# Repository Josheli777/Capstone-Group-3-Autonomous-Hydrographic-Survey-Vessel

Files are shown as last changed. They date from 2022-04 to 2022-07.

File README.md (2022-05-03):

# Capstone-Group-3-Autonomous-Hydrographic-Survey-Vessel

# Introduction: <br/>
Hydrography is the science of surveying and measuring different bodies of water, such as lakes, rivers, oceans, etc. These analyses are crucial for determining the shape of the water body. This data obtained from hydrography can be used to monitor the effects of climate change, beach erosion, and natural disaster prediction. Additionally, civil engineers must know the layout of a body of water before starting projects like dredging, diverting water sources, building docks, etc. The Tennessee Water Center currently has boats that take hydrographic projections that are remote-controlled; however, this technology is prone to human error and lacks efficiency that could be further improved by automation. There are currently autonomous vehicles that take measurements accurately and precisely. These boats take GPS coordinates and create parallel lines for the boat to travel to retreive less repetitious measurements.  The Water Center has contacted us to design a boat that has similar functionality to commerically avaialble hydrographic boats but at a significantly lower cost. The Water Center has asked that the boat can transmit GPS data and depth measurements in real time to allow surveyors to determine if data is accurate. If the data is not accurate, the team will be able to immediately bring the boat back to land base and not have to wait for the boat to complete its run. 

# Project Capabilities: <br/>
* Navigating bodies of water using a predetermined path
* Calculate its GPS location with centimeter level precision and accuracy
* Transmits GPS data and battery cell voltages for monitering
* Switches between manual and autonomous control through a remote controller switch
* Navigate bodies of water at a speed of 3ft/s for about 3 hours.

# Salient Outcomes: <br/>
## Battery Testing and Monitoring: 
The Water Center has requested that the autonomous hydrographic surveying boat have a run time of at least one hour and an accurate battery monitoring system. The current design of the power subsystem allows surveying teams to operate the boat for approximately 3 hours by use of 2 Liperior Lithium-Polymer batteries (14.8 V, 22000 mAh) connected in parallel. Additionally, 2 quad op-amp circuits were constructed and implemented that provide voltage readings of each cell in the Liperior batteries. These voltages can be verified by using the battery charging station that displays the actual cell voltages. 

## Data Transmission:
The specification to communicate data such as hydrographic measurements, GPS location, and battery voltage levels from the boat to a land base in real time has been addressed by the data transmission subsystem.  A pair of Arduino Unos and two nRF24L01+ radio modules were used in the subsystem design. The subsystem uses 2.4 GHz radio frequency (RF) to transmit the collected data to the base station PC. This system tested on Cane Creek, and it was confirmed that it could reliably transmit GPS data and battery voltage levels measured from the onboard battery monitoring system. The most up-to-date version of this system had a reliable connection at up to 550 meters and was transmitting GPS and battery data successfully. Additional work will be needed to complete the integration with the sonar system in order to transmit hydrographic data. 

## GPS Accuracy and Precision:
The use of Real-Time-Kinematic GPS receivers allowed us to achieve GPS data with much more accuracy than normal receivers. This project makes use of two simpleRTK2b receivers with a long-range transmission to receive latitude and longitude coordinates with centimeter level accuracy and precision. The two receivers are set up in a base and rover configuration. This allows the “rover” receiver, which is on the boat itself, to receive RTCM corrections from the “base” receiver which is connected to a PC on land. For this project, centimeter level accuracy and precision is required for the boat to navigate the predefined path. This can only be achieved if the location of the PC with the base station is known and uploaded to the base station receiver. After testing this configuration, the accuracy was found to be 2 cm and the precision was about 3 cm. 

# Video of Project Testing: <br/>
Full test (all systems communicating): https://youtu.be/emZcUE4ue-M

# Video of Experimental Analysis: <br/>
Battery Testing: https://www.youtube.com/embed/ibnFtC95N1E <br/>
Data Transmission Range Testing: https://www.youtube.com/embed/1JbO_NOVdsQ <br/>
Speed Testing: https://www.youtube.com/watch?v=HDup7zcuE3E&t=6s <br/>
GPS Accurcy & Precison Testing: https://www.youtube.com/watch?v=qKELYZJ67d8&t=15s <br/>
Switching Between Autonomous and Manual Control Testing: https://www.youtube.com/watch?v=emZcUE4ue-M&t=8s <br/>
Updated Battery Monitor: https://youtube.com/shorts/7BtCwoOhJbw?feature=share <br/>

Updated code attempting to navigate: https://youtube.com/shorts/_wtcSN0W4yQ <br/> 

# Images: <br/>
  Boat Prototype <br/>
  Autonomous Hydrographic Boat Prototype
 
# About Us: <br/>
The team members involved in the construction of the autonomous hydrographic boat are Andrew Alley, Carter Ashby, Levi Daniel, & Joshua Herrera. Mr. Jesse Roberts provided guidance and insight thoughout the duration of the project. This project was funded by Dr. Alfred Kalyanapu on behalf of the Tennessee Tech Water Center.

# Repository Contents: <br/>

### Project Documentation:
Bill of materials for the project and schematics for each subsystem.

### Reports:
Reports that document the design process for this project.

### Software:
Guides for installing computer applications, programming libraries, and operating systems necessary for this project.

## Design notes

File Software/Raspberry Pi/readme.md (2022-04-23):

# Raspberry Pi:
Parts Needed:
  * Keyboard
  * Mouse
  * 16 GB micro SD card
  * micro SD card reader
  * micro HDMI to HDMI cable
  * 5V 3A power cable

Installing Raspberry Pi OS
Download Raspberry Pi Imager:
https://www.raspberrypi.com/software/

* Insert micro SD card into PC using micro SD card reader
* Open Imager
* Click "Choose OS"
* Click "Raspberry Pi OS (32-bit)
* Click "Choose Storage" and select the inserted SD card
* Click "Write"
* Eject SD card when done

Setting up the Raspberry Pi
* Insert micro SD card into Raspberry Pi
* Connect mouse and keyboard
* Connect Raspberry Pi to monitor through left micro HDMI port using adapter cable
* Connect Raspberry Pi to power
* Follow on screen instructions to setup Raspberry Pi OS

Upgrade the Raspberry Pi:

```
sudo apt update
sudo apt full-upgrade
```
 
Install git if not installed already
```
sudo apt install git
```

Install pip
```
sudo apt get-install python3-pip
```

Install numpy
```
pip install numpy
```

Install proj
```
pip install proj
```

Install pyproj
```
pip install pyproj
```

Install stateplane
```
pip install stateplane
```

In order for the Raspberry Pi to interface with the GPS receiver, type the following command:
```
sudo raspi-config
```

Select Interfacing Options, Serial, No, Yes, Finish

Now you can use the python program above. <br/>

To enter a predetermined path into the program, enter a list of latitude points into the lats[] list and enter longitude points into the lons[] list.
Change the countyfips value to the one corresponding to your state and county.

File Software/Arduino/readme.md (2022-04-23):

# Arduino

## Software Description
Two Arduino Uno's are currently used to read GPS data, control the battery monitoring subsystem, and transmit/receive data using the nRF24L01+ radio modules.

### Rover Arduino:
The script "ROVER_full_function.ino" was written to control the Arduino on the rover. The serial baud rate should be set in 'setup()' to match the output baud rate of the simplertk2b GPS. Commands to start and configure the nRF24L01+ radio module and initialize pins for the battery monitoring task are also written in the 'setup()' function. The radio module is setup as the transmitter.<br/><br/>
The 'loop()' function contains the instructions for the primary functionality of the onboard Arduino. The program checks the Arduino's serial buffer for GPS data, and if data is found, it reads it and sends it to the radio module for wireless transmission. If no data is found in the buffer, a message that says "NoData" is transmitted by the radio module.<br/><br/>
Next, the 'BatteryCheck()' function is called. The function uses two GPIO pins to control the select lines of the 4 to 1 multiplexers. Two analog input pins on the Arduino are used to read the voltage levels of the multiplexer outputs. The program cycles through each of the battery cell voltage levels by changing the values on the select lines. The select line values are written to the appropriate pins in the 'SelectLineOut()' function. The voltages are converted from what the analog pins return to the actual voltage value. These voltage values are sent to the radio modules for transmission. The program continues by starting the next iteration of the 'loop()' function.

### Base Station Arduino:
The script "BASE_RX.ino" was written to control the Arduino at the base station. This Arduino will be connected to the technician's computer via its USB port. Commands to start and configure the nRF24L01+ radio module are written in the 'setup()' function. An if statement checks if the radio module starts successfully. The radio module is setup as the receiver.<br/><br/>
The 'loop()' function checks if the radio has received any transmissions, and if it has, it reads the information and outputs it to the Arduino serial buffer.

## Dependencies
The Arduino SPI library is used in both scripts to communicate to the nRF24L01+ modules using SPI protocol.<br/><br/>
The external RF24 library is used to control the radio modules in both scripts. https://github.com/nRF24/RF24 <br/><br/>
The Arduino SoftwareSerial library is used by the rover Arduino to make two GPIO pins (2,3) function as serial pins (TX/RX).

## Installation
Both .ino files can be downloaded and opened in the Arduino IDE. To upload the scripts to the Arduinos, connect the computer running the IDE to the USB port of the approprate Arduino and select "Upload". Note that the .ino files must be in a folder of the same name (excluding the '.ino') to upload properly. When the "Done uploading" message is displayed, the program will now execute on power-on until it is overwritten by another program. For more details on using the Arduino IDE follow https://docs.arduino.cc/learn/starting-guide/the-arduino-software-ide

## How to Operate
Refer to the design schematics to connect power and onboard components to the rover Arduino. The uploaded program will execute at power-on.<br/><br/>
The base station Arduino should remain connected to the base station computer via USB. The data received from the rover can be viewed by clicking Tools->Serial Monitor and changing the baud rate to match the baud rate set in the "BASE_RX.ino" script.

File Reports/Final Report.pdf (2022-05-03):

# Autonomous Hydrographic Survey Vessel

Andrew Alley
Department of Electrical
Engineering
Tennessee Tech University
Cookeville, TN
atalley42@tntech.edu

Carter Ashby
Department of Electrical
Engineering
Tennessee Tech University
Cookeville, TN
cashby42@tntech.edu

Levi Daniel
Department of Electrical
Engineering
Tennessee Tech University
Cookeville, TN
lbdaniel42@tntech.edu

Joshua Herrera
Department of Electrical
Engineering
Tennessee Tech University
Cookeville, TN
jherrera42@tntech.edu
I. INTRODUCTION
Bathymetry is the science of measuring and observing the depths of different bodies of water, such as lakes, rivers, oceans, etc. These analyses are crucial for determining the shape of the water body. Furthermore, data obtained from bathymetry can be used to monitor the effects of climate change, beach erosion, and subsidence. The Tennessee Tech Water Center also uses bathymetry to create simulations to predict natural disasters and locations that are more susceptible to flooding.

The Water Center currently uses remote-controlled boats that take bathymetric projections by navigating the boat back and forth across the body of water. Performing this task manually is labor-intensive and prone to error. Depending on the size of the body of water, it could take several days to collect all the necessary data. The resolution of the data is also too low to create a useful bathymetry map. There are autonomous hydrographic survey vessels (HSV) commercially available; however, these products greatly exceed the budget of the Water Center with autonomous HSVs starting at a price of $70,000.

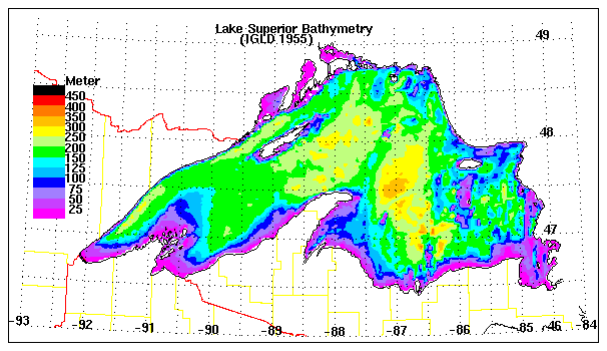
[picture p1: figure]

Figure 1: Bathymetry Map of Lake Superior

A. Overall Idea
The requirement to deliver a boat that will navigate the entirety of a body of water without direct control from the user will be met by constructing a watercraft driven by software that intelligently plots and follows a course that will allow the boat to collect measurements over the full area of the body of water. To collect the required bathymetry data samples the boat will be equipped with sonar and GPS. A sonar sensor is the most likely solution for depth measurement device. An accurate GPS-generated location reading will be recorded with each sonar measurement, and data processing software will be used to generate maps and charts from the collected data. A software application will also be developed that will allow someone onsite to transmit commands to the boat while also being able to view the collected bathymetry data in real time.
B. Constraints and Regulations
The boat was given these initial specifications:
- The boat must successfully measure the entirety of Cane Creek Lake (56 acres) in one test run
- The boat needs to travel at a speed of 3-5 ft/s to ensure accurate sonar data measurements
- Data such as hydrographic measurements, GPS location, and battery voltage levels need to be transmitted from the boat to a land base in real time.
- The users on the land base need to be able to switch between manual and autonomous control.
- Obstacle avoidance needs to be implemented to prevent any collisions when the boat is in autonomous control.
- An abort option needs to be implemented if the boat is receiving inaccurate data measurements.
- The overall design and construction price should not exceed commercially available HSVs.
- The design must be easily replicable for any group interested in using this project to take their own hydrographic measurements.

The regulations that govern remote control radio signals require that the boat only be controlled via radio signals in the 26-28 MHz band and that power output from the transmitter be no more than 4 Watts. The radio signals used to control the boat must also only control the boat; they cannot be used to transmit data from the collection process [5].

The regulations that govern Wi-Fi signals require that Wi-Fi frequencies be restricted to 902-928 MHz, 2400-2483.5 MHz, or 5725 to 5875 MHz, as they are considered unlicensed wireless equipment devices [6]. The transmitter is also required not to exceed a peak output power of 1 Watt, and the Effective Isotropic Radiated Power (EIRP) cannot exceed 4 Watts [7]. The EIRP is simply a combination of the output power and the antenna gain.

II. SALIENT OUTCOMES

A. Battery Capacity and Monitoring:
The Water Center has requested that the autonomous hydrographic surveying boat have a run time of at least one hour and an accurate battery monitoring system. The current design of the power subsystem allows surveying teams to operate the boat for approximately 3 hours by use of 2 Liperior Lithium-Polymer batteries (14.8 V, 22000 mAh) connected in parallel. Additionally, 2 quad op-amp circuits were constructed and implemented that provide voltage readings of each cell in the Liperior batteries. These voltages can be verified by using the battery charging station that displays the actual cell voltages.
B. Data Transmission:
The | specification | to | communicate | data | such | as
hydrographic measurements, GPS location, and battery voltage levels from the boat to a land base in real time has been addressed by the data transmission subsystem. A pair of Arduino Unos and two nRF24L01+ radio modules were used in the subsystem design. The subsystem uses 2.4 GHz radio frequency (RF) to transmit the collected data to the base station PC. This system tested on Cane Creek, and it was confirmed that it could reliably transmit GPS data and battery voltage levels measured from the onboard battery monitoring system. The most up-to-date version of this system had a reliable connection at up about 550 meters and was transmitting GPS and battery data successfully. Additional work will be needed to complete the integration with the sonar system in order to transmit hydrographic data.
C. GPS Accuracy and Precision:
The use of Real-Time-Kinematic GPS receivers allowed us to achieve GPS data with much more accuracy than normal receivers. This project makes use of two simpleRTK2b receivers with a long-range transmission to receive latitude and longitude coordinates with centimeter level accuracy and precision. The two receivers are set up in a base and rover configuration. This allows the “rover” receiver, which is on the boat itself, to receive RTCM corrections from the “base” receiver which is connected to a PC on land. For this project, centimeter level accuracy and precision is required for the boat to navigate the predefined path. This can only be achieved if the location of the PC with the base station is known and uploaded to the base station receiver. After testing this configuration, the accuracy was found to be 2 cm and the precision was about 3 cm.

III. OUTLINE OF REPORT
The objective of this paper is to present the problem that this project aimed to solve and the steps in developing the solution. The goal of this project is to develop an autonomous machine that measures the depth of bodies of water. These measurements will then be used to create an accurate bathymetry map of the lake, river or pond that is being mapped.

The rest of this paper will describe the science and engineering behind this project and the process by which this project was completed.

IV. LITERATURE REVIEW
Two of the commercially available products for autonomous HSVs are the CEE USV from CEE Hydro Systems, and the Seafloor HyDrone-RCV survey boat by FLT Geosystems. Both boats allow the user to switch between manual and autonomous navigation. They are both used for taking hydrographic surveys of bodies of water using autonomous navigation. We modeled our original idea for the navigation program after these products.

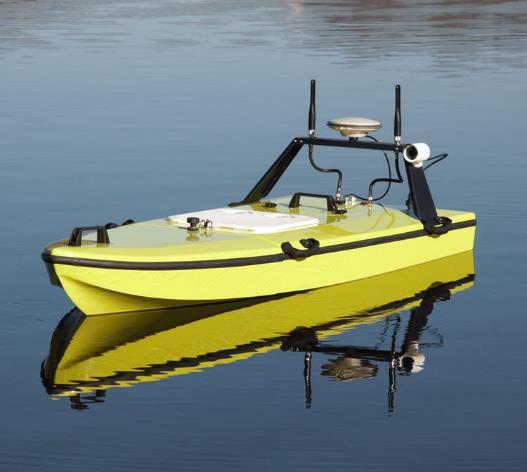
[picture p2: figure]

Figure 2: CEE USV

The main difference between our project and these products is the cost and functionality of the devices. The CEE USV has been noted to be upwards of $70,000 and the HyDrone-RCV with the autonomous navigation upgrade is around $15,000. One of the biggest cost cuts came from the RTK GPS receivers. The CEE USV uses a receiver that is well over a few thousand dollars while we are using a simpleRTK2b receiver kit which is less than $900 [12].

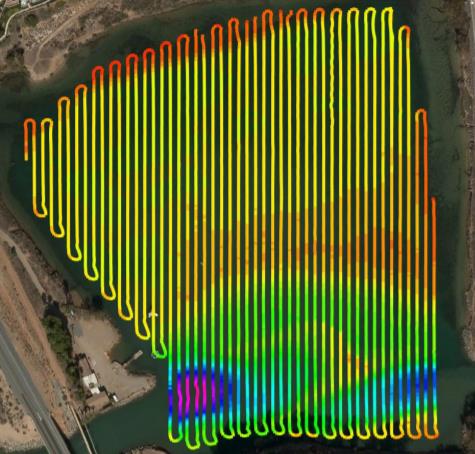
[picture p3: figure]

Figure 3: Intended Path Generation Method

The method of autonomous navigation is also a significant difference between the commercial products and our project. This model uses a predefined path that is specific for the body of water that needs to be surveyed. These paths can be easily generated using path planning software such as ArduPilot. The

GPS points can be entered into the autonomous program and the Raspberry Pi will process them and use them as waypoints.

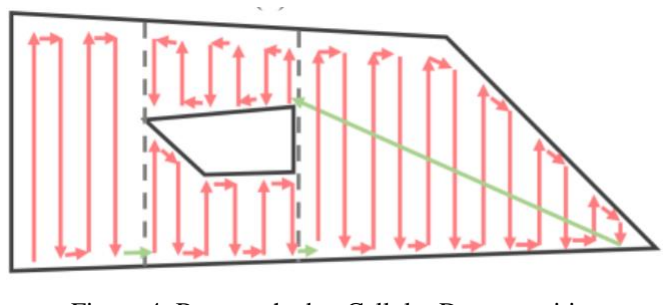
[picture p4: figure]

Figure 4: Boustrophedon Cellular Decomposition

Originally, we planned to use an algorithm known as Boustrophedon cellular decomposition. This is a commonly used path planning method to effectively cover large surfaces such as fields [13]. Autonomous lawn mowers use this method to cover entire fields efficiently. This method involves splitting an area up into sections and determining the best path to follow in order to minimize travel distance and travel time. Unfortunately, we were not able to incorporate this due to time. So, the previously mentioned method of predefining a path was used instead.

V. DESIGN PROCESS
The Water Center has asked us to develop an autonomous vessel that is capable of navigating a given body of water. The specifications include that the boat should be able to navigate Cane Creek Lake within its battery life as well as travel at optimal speeds for bathymetric data collection. The boat must also be able to transmit data back to an on-land computer. The design that was implemented for this project includes a navigation system, power system, and data transmission system. The purpose of the navigation system is to make the boat autonomous while keeping the boat at a specified speed and keeping the boat on a path that is optimal for bathymetric data collection. The power system is responsible for distributing power to each component and regulating voltage supplies. The data transmission system transmits GPS data, battery voltages, and eventually sonar data.
A. Original Navigation System
The manual control portion of the navigation system will assist in meeting the specifications that the boat will be autonomous and that the boat will have an abort operations function. For the boat to be able to autonomously navigate the body of water, the GPS coordinates of the perimeter of the lake must be measured. This process will require the user to manually drive the boat around the lake with a controller. The manual control system also needs to have programmable inputs for the abort function. In an emergency the user will press a button on the manual controller that tells the boat to stop collecting sonar data and return to the user. The user will also be able to tell the boat when to start collecting perimeter data, when to switch to manual control, and when to begin autonomous navigation. These will be assigned to inputs on the remote controller by the user. These functions were determined to be necessary to improve autonomy or ease of use.

The components that will be used for this system include the Spektrum DX6E controller and the Spektrum AR620 receiver. The decision to use this controller and receiver is based on its available programmable switches and its ability to operate the current boat model that was built by the Water Center at TN Tech. This was observed when a test run was conducted with the current boat model on Cane Creek Lake. The Spektrum controller will allow the project to meet the specification that the boat will be able to collect bathymetric data, the boat will be autonomous, and the boat will have the ability to abort data collection in case of an emergency. For the boat to begin collecting bathymetric data, it will need to be driven manually around the perimeter of the lake so that GPS data for the lake can be recorded. To do this, the Spektrum controller and receiver will need to output a signal that can control the electronic speed controllers (ESCs) that control the motors of the boat. This was observed by test driving the current model of the boat which implemented the Spektrum controller and receiver as well as Blue Robotics Basic ESCs and Blue Robotics T200 brushless thrusters. These are the same ESCs and thrusters that will be implemented in the autonomous boat. The range for the receiver is listed as 2 kilometers [1]. This distance is suitable for the purposes of navigating Cane Creek Lake. The length of Cane Creek is just over half a mile and since the user must always be able to see the boat, it will be easy for the user to stay within range. This controller also has extra switches on it that can be programmed for desired functions [2]. These switches can be assigned to the receiver outputs which will connect to the Raspberry Pi 4 in the onboard navigation system. These will control the boat’s mode of operation.

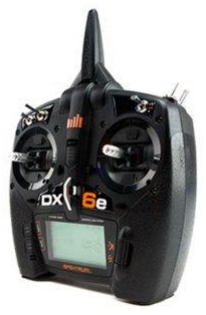
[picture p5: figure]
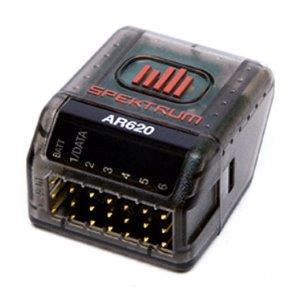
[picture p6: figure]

Figure 5: RC controller and Receiver

B. Navigation System (Autonomy)
The autonomous portion of the navigation system will directly meet the specification that the boat will be autonomous. It will use a GPS device to record data for the perimeter of the body of water. A microcontroller will process this data and create a path for the boat to travel that is optimal for sonar data collection. The microcontroller will then send signals to the motors that control the thrust to steer the boat along the created path. Signals from the user will be sent to the microcontroller to adjust the boat’s mode of operation.

The Blue Robotics T200 thrusters are currently what the Water Center has for an old model of the boat. The Blue

Robotics T200 thruster will be able to meet the specification that the boat should move at 1-3ft/s. Using the CAD files for the hull of the boat, an estimate of the weight was calculated. The total volume of the hull was found to be 9,381 cm^3. To be safe with the calculation of the hull’s weight, the highest density 3D printed material was used which was 2.16g/cm^3. Multiplying these two values results in a total weight of 20.264kg. This equates to an estimated weight is 44.67lb. The total weight of the hull and other components turns out to be about 52.18 lb. The maximum thrust of the T200 motors is 11.6lb of force [3]. Assuming the boat will accelerate to the desired speed of 3 ft/s or 0.9144 m/s within 1 second, the acceleration will need to be 0.9144m/s/s. Using the equation F = m*a, the force needed to accelerate a mass of 52.18lbs or 23.67kg at a rate of 0.9144m/s/s would be 21.64 Newtons or 4.86lbf. This is well within the capabilities of the T200 motor.

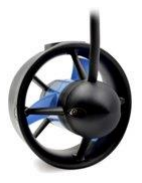
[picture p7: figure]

Figure 6: T200 Thruster

The Blue Robotics ESCs will be able to control the motors since these ESCs are specifically designed to control T200 or T100 motors. These ESCs are what the Water Center is currently using for their model of the boat. Here is a performance chart that displays the thrust of the T200 motor with different operating voltages while using the Blue Robotics Basic ESC R3 [3]. From the chart the thrust is highly adjustable using the Basic ESC R3 and adjustments to the operating voltage.

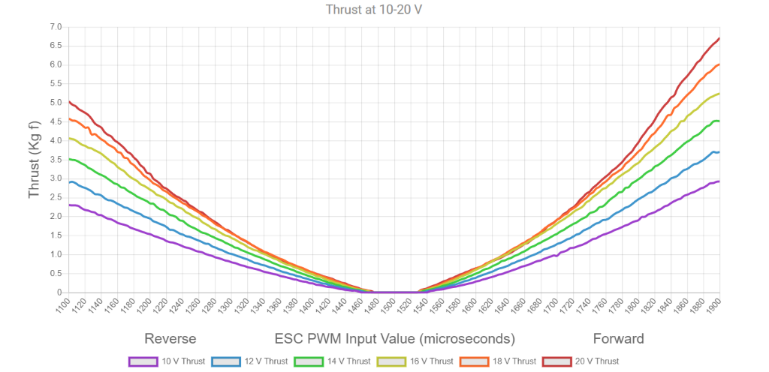
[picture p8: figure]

Figure 7: T200 Thruster Performance Chart

Figure 8: Blue Robotics Basic ESC

The Raspberry Pi 4 is necessary to meet the specification that the boat will be autonomous. The Raspberry Pi 4 will have ROS installed and the appropriate drivers necessary to process the GPS data from the simpleRTK2b board. The Raspberry Pi 4 will be capable of controlling the ESCs based on the documentation for both components. There are designated pins on the Raspberry Pi that can produce a PWM signal which is the required input signal for the ESCs [4][5]. Also, the voltage output of a Raspberry Pi 4 is 3.3V which is within the 3.3V-5V range required for the operation of the ESC [4][5].

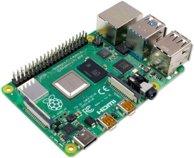
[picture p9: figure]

Figure 9: Raspberry Pi 4 B

The simpleRTK2b long range kit will allow the project to meet the specification that the boat will collect bathymetric data and that the boat will be autonomous. This kit will allow the Raspberry Pi to know its latitude and longitude to within a few centimeters [6]. The boat will be driven around the perimeter of the lake before the sonar data collection begins. The GPS data for the perimeter of the lake will be processed by an ROS program in the Raspberry Pi to create a path that the boat will travel while it is collecting bathymetric data. Centimeter level accuracy is necessary to produce sufficient data to create bathymetric maps. The simpleRTK2b LR kit will be able to communicate NMEA protocol data messages that contain the GPS coordinates [6]. This kit provides two simpleRTK2b boards. They will be set up in a “base and rover” configuration in which one board will be on the boat and one will be in a fixed position with a clear view of the sky. This allows the position of the boat to be calculated to within a few centimeters. This is necessary for the generated path to be optimal for sonar data collection. The GPS data is transferred between the boards using two antennas and two XBee radio modules [6]. The range of this kit is 10 km which exceeds any limitation set by the controller or other systems [6].

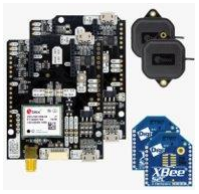
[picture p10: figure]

Figure 11: SimpleRTK2b Long Range Kit

The 4-channel mux will assist in meeting the specification that the boat will have an abort function. In case of an emergency, the user will flip a switch on the Spektrum RC controller. This will send a signal to the Raspberry Pi which will toggle one of the select lines on the mux [7]. The output of the mux will switch from the Raspberry Pi's motor control signal to the RC receiver's motor control signal. The simpleRTK2b adapter for the Raspberry Pi 4 will be used for its intended use case which is to connect a Raspberry Pi 4 to a simpleRTK2b board [8].

C. Navigation System Changes
The original design of the navigation system included a microcontroller, steering mechanism, manual control, mapping software, obstacle avoidance system, and a GPS system. While most of these components and concepts remained, the functions of each component were changed. For the microcontroller, we ended up using a Raspberry Pi 4b with 4 GB of RAM. The intended functions of the Raspberry Pi included processing GPS data, sending GPS data to a mapping software on an on-land PC, controlling the thrusters to keep the boat on the generated path, and to avoid obstacles. Of these functions, the final product processed GPS data and controlled the thrusters. We decided that obstacle avoidance would be taken care of by switching the boat to manual control and driving around the obstacle. The original plan for generating the path was by recording the perimeter of the lake and having the Raspberry Pi process the data and generate a zig-zag path across the lake. In the end we decided that software such as Ardupilot could be used to generate the waypoints of the path and the Raspberry Pi will handle the rest. Switching between manual and

Figure 10: Full Navigation Schematic

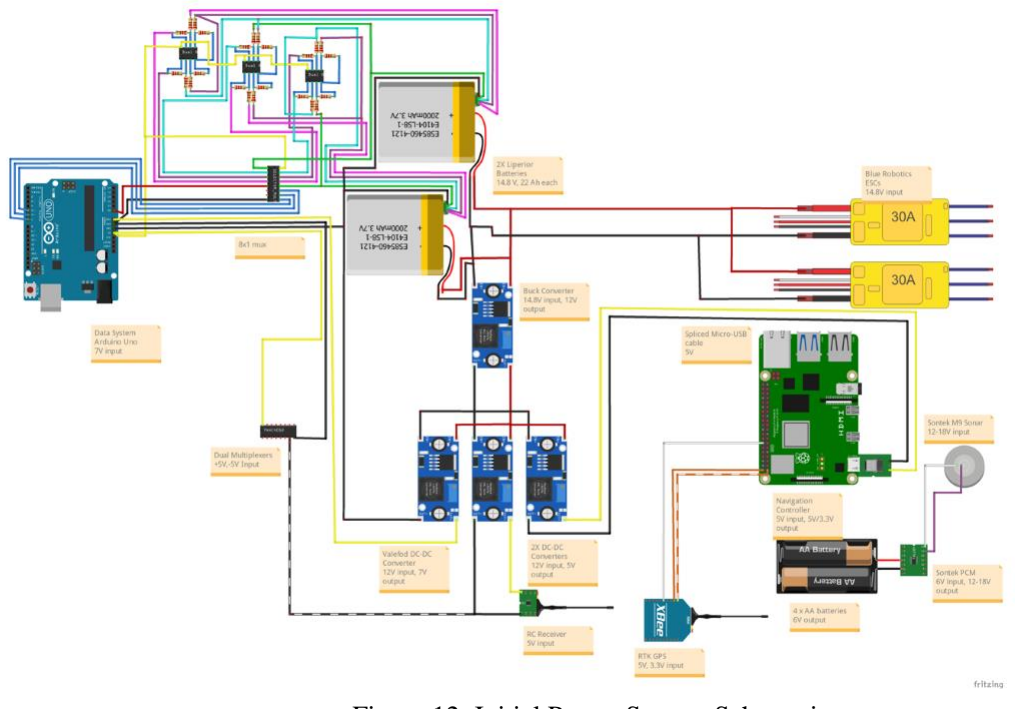
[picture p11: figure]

autonomous was originally going to be done by sending a signal to the Raspberry Pi through the remote control. Then Pi would then control the select lines of an analog mux that switched which device was controlling the thrusters. The use of ROS to create the autonomous program was scrapped as well due to issues with installation and usability of Ubuntu Mate. We ended up using Raspberry Pi OS which is not compatible with ROS.

D. Power System Initial Design:
Understanding the power requirements for each individual component was critical to the decision on battery selection. A compromise was necessary to balance the physical size and weight of the battery or batteries in order to keep the boat afloat and maneuverable, with the voltage and current it could supply and the period of time it could last. It was determined that two 14.8 V, 22000 mAh batteries were the best choice. They weigh 3.75 lbs each, which is negligible compared to the weight of the boat and its buoyancy. Connecting the two batteries in parallel extends the time that the given capacity can last, as the electronic systems draw power from each boat evenly, reducing the drain on a single battery by 50%.

These batteries are needed to provide the appropriate voltages to the Arduino, Raspberry Pi, and RC receiver. To address this, a buck converter was implemented on each component with the batteries as the input. The output of a buck converter is directly proportional to the input by what is known as a duty ratio. If the input voltage of a buck converter was to increase, the output was also decrease at a proportional rate, and if the input voltage of a buck converter decreases, the output also decreases. The input of the buck converters needed to maintain a constant voltage even though the batteries’ voltages would eventually decrease. A buck-boost converter was then designed into the circuit to provide a constant 12 V to the buck converters.

Both buck and buck-boost converters output voltages with some ripples. These ripple voltages described in their datasheets were too large and would damage the components if left as is. To rectify this issue, filters were placed at the outputs of all the converters.

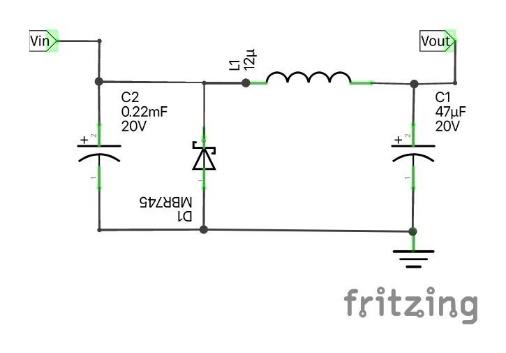
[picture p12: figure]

Figure 13: Buck Filter

Measuring the batteries voltage output was necessary for monitoring the capacity, since the battery voltage must be within an optimal range for the ESCs to operate. If the battery drops below this voltage, the operation will be less than optimal. The voltage measured by the Arduino Uno will be compared to the optimal voltage. If it is less than the optimal voltage, the Arduino Uno will send a signal to the Pi. The Pi will change the course of the boat to the starting point so that the user can recharge the batteries. The Liperior batteries consist of 4 cells that are each 3.7 V. The voltage of each cell needs to be above 3.5V to be within optimal operating voltage. If the batteries drop below this voltage, there is a risk of damaging the batteries. The batteries have a balance plug that is connected to each of the cells in the battery. These were used to measure the voltage of each of the cells. The Arduino Uno compares each of the 8 battery cells voltages to see if they are above 3.5 volts. This was done using an 8x1 multiplexer and differential amplifier circuits. The Arduino Uno is only capable of measuring voltages of up to 5

Figure 12: Initial Power System Schematic

V. Since the batteries are connected in series, the output voltages from the balance plugs were predicted to be 3.7 V, 7.4 V, 11.1 V, and 14.8 V. There were going to be 6 differential amplifier circuits. The team planned to use 3 dual op amp ICs. Each circuit used would have consisted of four 1.0 kΩ resistors. The output would have been the difference between two of the battery cells. An 8x1 mux will be used to multiplex the voltages. The Arduino controls the select lines and "loop" through the voltages and measure each battery cell. The multiplexers and the dual op-amps were to be powered by the same 5V pin that is powering the other mux. The mux needs between 4.5 and 5.5 volts to power it.

The thrusters have a maximum current draw of 20 A at 14 V each, when operating at full throttle. The required thrust calculated to maintain the specified boat speed was approximately 4.86 lb*f or 2.20 kg*f. The thrusters can provide this amount of force while drawing approximately 6 A at 14 V. This was assumed to be the average current required from a single thruster. The Raspberry Pi 4 B itself has a maximum current draw of 3 A and 1.2 A for any peripheral components, such as the GPS device. The Arduino board has a wide range of current draw depending on the purpose of operation, with the maximum being approximately 100 mA. The RC receiver, when the boat is operating in manual mode, will allow the thrusters to draw the same amount of current that they would draw operating in autonomous mode. The maximum continuous current draw for the receiver itself is 3 A. Then the total average current draw of all systems during normal operation is approximately 21.87
A. The current draw may have been more or less, depending on the throttle of the motors, data collection, and data transmission. Each Liperior battery has a capacity of 22 Ah. When connected in parallel, the combined capacity will be 44 Ah, which will provide a runtime for the boat of approximately 2 hours. This met the Water Center’s desired specification to have the
autonomous | boat | operate | for | at | least | 1 | hour.
E. Power System Changes:
Once the team received the desired components, circuit construction and analytical testing were done by using solderless breadboards. The buck converters were sufficient in outputting the required voltage ranges of operation to the Raspberry Pi, Arduino, and RC receiver. The filters were successful in reducing the ripples of the buck converters from 60 mV to approximately 30 mV. When testing the buck-boost converter, however, the output ripple was significantly larger than predicted. The designed filter’s capacitors were then modified in a series of analytical testing to reduce this ripple, but testing proved unsuccessful. The team then backtracked and reviewed the behavior of the buck converters that were received. The output of a buck converter was set to 5.0 V, and the input was set to 14.8 V on a DC power supply. This input was then changed to determine how the output voltage would be affected. It was concluded that the buck converters kept a constant output voltage if the input was at least 1.0 V greater than the output. The team then concluded that the buck-boost converter was not necessary and removed it from the power subsystem.

Once the batteries came in, the balance plug could be tested. It was found that all 4 cells of each battery would need to be implemented into the differential amplifier circuits. Instead of using 3 dual op-amps, the team decided to use 2 quad op-amp

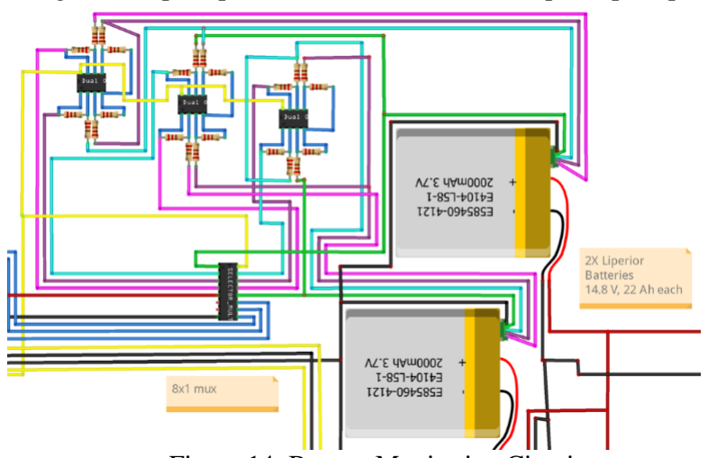
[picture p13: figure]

Figure 14: Battery Monitoring Circuit

circuits with 4 equal resistors with each individual circuit. Another issue arose when observing the output pins of these circuits. Most of the pins would output accurate readings, but some pins would have voltages ranging from 5-10 V. This was due to the lack of negative voltage supply that the team initially thought was unnecessary. A temporary solution was to use two 9 V batteries with one of the polarities reversed. This was not optimal for the final design, for teams would not be able to realistically monitor the capacities of the 9 V batteries. This was then addressed by implementing an inverter IC. The input of the IC is the Liperior batteries. The positive output is connected to V⁺

, and the negative output is connected to V⁺
. Testing then
verified that the voltages of the outputs were consistent with the individual battery cell readings that are displayed on the battery chargers.

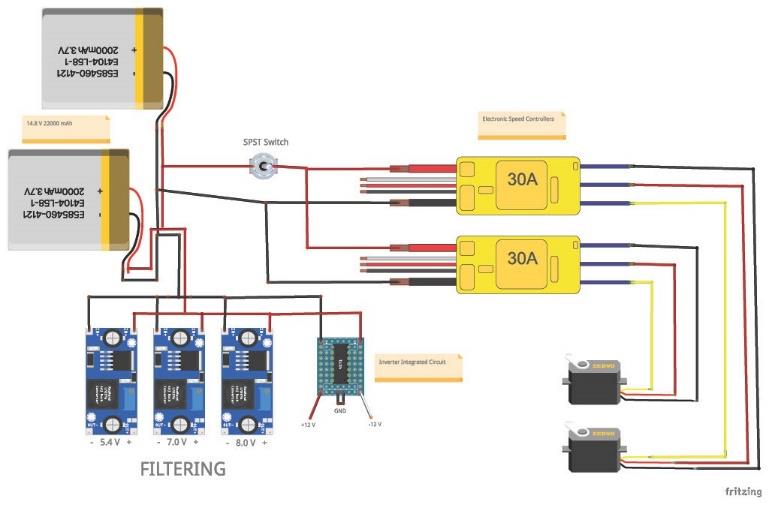
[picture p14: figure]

Figure 15: Final Power System with Dual V+ and V- Supply

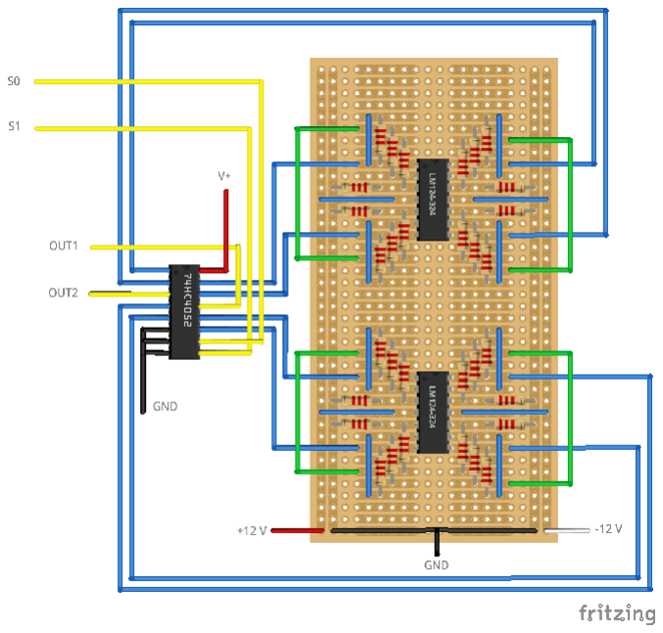
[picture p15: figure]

Figure 16: Updated Battery Monitoring Circuit

F. Transmission System Initial Design:
To meet the requirement to observe data in real-time as it is collected, a system has been designed to collect measured data and transmit it to a local computer system so it can be viewed by the user. The design of this system has evolved over the course of this project according to new knowledge and changes of ideas.

The original conceptual design of the data transmission system was split into two main parts: the base station section and the onboard section. The design for the onboard section included a microcontroller to collect data from the onboard systems and an RF transmitter to send the data to the base station. The design for the base station section included a microcontroller and an RF receiver. The microcontroller was connected to the base station PC with a USB connection, and it was designed to be used to operate the RF receiver and communicate the received data to the PC. Also, the designs assumed the SonTek HydroSurveyor sonar system would be used and included the SonTek Power and Communications Module (PCM) as the primary method for the transmission of hydrographic depth data.

When first selecting components for the conceptual system, a pair of 433 MHz RF modules was selected for the transmitter and received components. At the time of the detail design, the decision was made to use 2.4 GHz modules instead. The first reason this change was made was because in the United States the 433 MHz frequency band is restricted by the FCC to only certain licensed devices. Secondly, although 433 MHz frequency transmitters offer much greater range for the same transmission power, 2.4 GHz devices can support much greater message signal bandwidths. In addition, the connection for the onboard GPS module to the onboard microcontroller was intended to be from the microUSB connection on the simpleRTK2B GPS module to the USB-B port of the microcontroller. This connection was later redesigned to be made via a serial UART connection between the TX/RX pins of the GPS and microcontroller.

G. Transmission System Updated Design:
The nRF24L01+ PA LNA wireless transceiver modules were selected for the transmission and reception of collected data. These modules support programmable output power and have a low power consumption. Available output power levels include 0 dBm, -6 dBm, -12 dBm or -18 dBm, and the module only consumes around 12 mA during transmission at 0 dBm. All the parameters can be configured through a Serial Peripheral Interface (SPI). This type of interface uses the concept of Master and Slave. In this case the microcontroller was the Master, and the transceiver was the Slave. Also, this version of the nRF24 module uses an external antenna, a power amplifier, and a low-noise amplifier to increase the transmission range from 100 meters to up to 1000 meters, a distance that satisfies the range specification.

Both the base station section and the onboard section will use a microcontroller and an nRF24L01+ PA LNA wireless transceiver module with the same connections. The schematic detailing these connections can be seen in the figure below. The radio frequency receiver module receives a message signal encoded with collected data and will decode the signal to extract the measurement data. The microcontroller was designed to control the radio frequency modules that receive an encoded radio wave. Once it has been decoded, the microcontroller will transport the received measurement data to a connected computer via a USB-B to USB-A serial connection. In addition, the SonTek radio dongle will be connected to a USB port on the computer and will receive measurement data collected by the M9 and transmitted from the PCM.

The Arduino Uno was selected to be used as the microcontroller for each section because of its ability to handle various baud rates, utilize analog and digital input/output header pins, and communicate with other devices over different digital communication protocols simultaneously. Specifically, the Uno can communicate using an SPI, making it compatible with the selected RF transceiver for data transmission. The GPS module was confirmed to meet the specifications for a GPS compatible with the Hydrosurveyor M9. The specifications were as follows:

- Data output rate between 1-10 Hz (10 Hz recommended)
- Baud rate set to 38400
- NMEA output sentences: GPGGA and GPVTG (if used for position) and/or GPHDT (if used for heading).

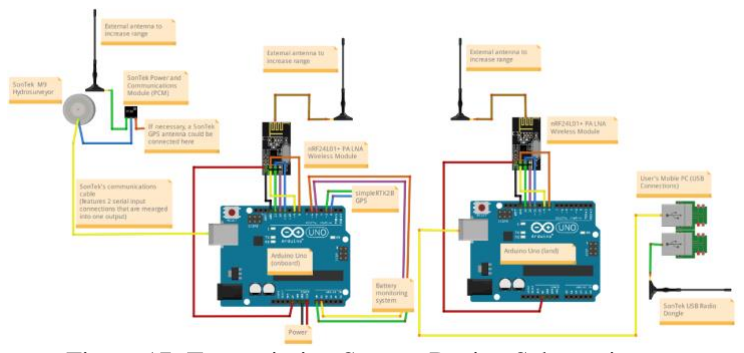
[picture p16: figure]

Figure 17: Transmission System Design Schematic

VI. SAFETY
With any autonomous system, the first major concern is how the system interacts with humans and other living creatures. In the case of an autonomous vehicle, the concern is that the vehicle must be able to stop operation when its actions are detrimental to life or limb. For a hydrographic survey vessel, there may be people or animals swimming in the lake or river that it is scanning, and an autonomous HSV must not provide risk to those people or animals it may encounter.

The design of this specific boat relies on the responsibility of the on-site technician to recognize and mitigate any potential risks. This autonomous boat is equipped with a manual override system, which immediately stops the boat and gives control to an operator when activated. This system is activated by a switch on a Radio-Controlled device that also functions as the controller when in manual operation. This autonomous system is not designed to be operational without supervision. A technician must be present while the boat is in operation and must be aware of the water body and the presence of any humans or animals or other non-living obstacles in order to manually drive the boat in areas where human precision is required.

VII. RESULTS
The Water Center had a specification that the autonomous boat must be able to successfully drive the entirety of Cane Creek Lake (0.2266 km^2) in one run. The base station was set up at the dam of Cane Creek Lake and the boat drove along the dam 56 times at a constant speed of 3-5 ft/s. The speed was determined by using the speeds used by the Water Center to obtain accurate depth measurements. The boat was kept close to the dam due to the boat not being completely waterproof. The inside of the hull was not coated in fiberglass, which allows water to get into the hull and weigh it down. If the boat was to have an issue with water getting in the hull, the team could easily get the boat out of the lake and prevent any damage to the circuits. The battery monitoring circuit showed that the voltages of each cell were 4.2 V, and when the batteries are considered "low", the voltage is approximately 3.5 V. The boat successfully drove the distance determined to be equal to the area of Cane Creek Lake. The team then determined how long the boat could run, and it was concluded that the boat could remain fully operational for approximately 3 hours. The test came to an end when the team noticed that the thrusters started to slow down after full thrust, thus becoming a risk if the boat was hypothetically in the middle of the lake. Additionally, the battery monitoring circuit was transmitting data to the land base, which showed that the cells in the batteries had a voltage of 3.7 V.

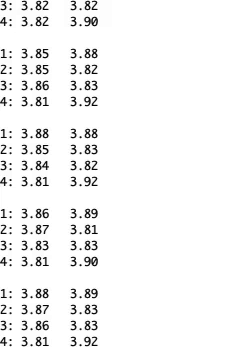
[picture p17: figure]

Figure 17: Live Data Stream of Battery voltages

To test the product’s ability to transmit collected data wirelessly, the base station was set up at the dam of Cane Creek Lake, and the boat drove away from the base station until accurate data could not be obtained. The transmitter was operating with a transmission power of -6 dBm. The final distance the Arduino was able to receive data was approximately 1200 feet or 365 m. The team also tested the range on campus because the hull was taken to get coated in more fiberglass. One team member stood outside of Foster Hall on Tennessee Tech's campus with the laptop and land radio module, while two other team members carried the rover radio module down University Drive until the land module could not receive any data. The transmitter was operating with a transmission power of -6 dBm. Data transmission slowed down once the team members crossed North Willow Avenue going towards Tech Village. The last received transmission was at about 596 m.

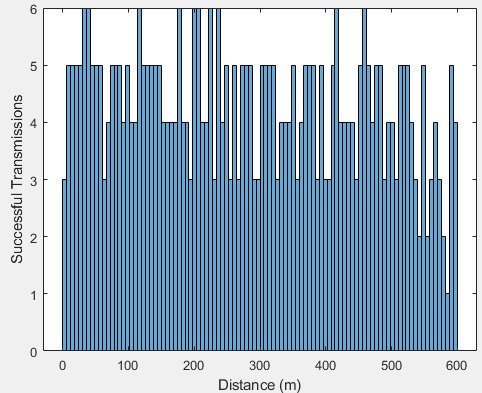
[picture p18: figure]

Figure 18: Number of Transmissions vs. Distance

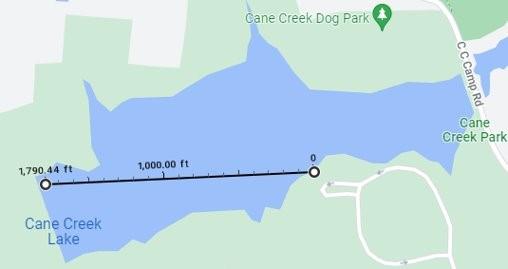
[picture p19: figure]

Figure 19: Experiment Location and Transmission Distance

Using two simpleRTK2b receivers, the accuracy and precision of the recorded GPS data was observed. The receivers were in a base and rover configuration. Using just the rover receiver, the GPS coordinates were accurate to within 1.4 meters and precise to within 10 centimeters. Using the base station and the rover, the accuracy was around 1.9 meters, and the precision was 2 centimeters. The base station and rover were tested again with the known location of the base station uploaded to the base station receiver. The accuracy was withing 2 cm and the precision was within 3 cm.

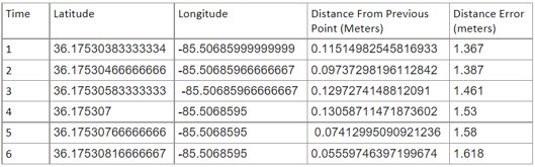
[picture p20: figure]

Figure 20: Rover Data

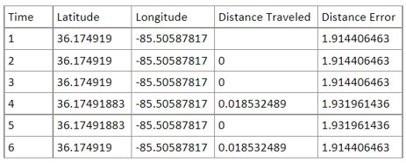
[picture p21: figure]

Figure 21: Base and Rover Data

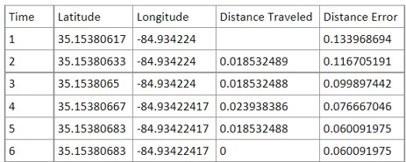
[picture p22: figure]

Figure 22: Base and Rover (Preset Location) Data

VIII. TIMELINE
The goals that the team chose to pursue, and the order of priority were determined by the necessity of each subsystem to the boat. As illustrated by the Gantt chart, some of the major goals for the project were to identify specifications and constraints, complete a detailed design and analysis for all subsystems, implement and integrate all subsystems, debug all software, and test the final prototype.

The order of these goals presents a linear progression of the project and makes it a logical projection for the completion of goals. There was also some room allowed for overlap across goals so that progression was not prevented by a delay in completion of previous goals. Once the specifications could be identified for a particular subsystem, design could begin for that

subsystem without waiting for all specifications for all systems to be finished. In the case of implementation and integration, software could be written and tested at the same time other circuits were being built and integrated into the overall design without interfering with the software or other systems.

Specifically, the team had goals to build a self-contained, battery-powered system, which could plot a path around a body of water, navigate that path autonomously, transmit its GPS coordinates and its battery levels to an on-shore computer, and would have the ability to switch into manual operation at the user’s discretion. While the specifications came directly from the Water Center, the goals were set to meet these specifications in the most efficient manner for the team to have a final product. Subsystems with specifically desired features were addressed with higher priority, and additional features were addressed as there was opportunity to include them.

Tasks were planned based on these major factors: predicted duration, urgency, and difficulty. The navigation subsystem, for example, was anticipated to take a lot of time to design and implement due to potential troubleshooting and experimental analysis. Furthermore, it was crucial that autonomous navigation have a solid foundation, for this was the most prioritized specification made by the Water Center. These reasons are what made the team plan to have navigation take up the most time on the Design Phase 2 Gantt chart as shown below. Other subsystems were expected to have a shorter time of completion, so these were not as urgent as the navigation system. These systems could also be tested in the lab at any time, whereas the navigation system had to be tested in a body of water when the weather is in optimal condition.

The team would have one meeting a week discussing progress on individual tasks as well as determining the next realistic step for the project’s construction. Members informed the other teammates if they believe that the individual tasks could not be completed by the next deadline. The team provided assistance if necessary and did not hold these moments against one another. If a group task was not completed by the desired deadline, the team would continue to work on that task as well as starting ones of less difficulty but of equal importance.

When distributing tasks amongst the team, the members discussed each other’s strengths and weaknesses. Joshua Herrera excels in programming languages such as Python, C, and C++. The Water Center required that the boat could send bathymetric measurements and GPS coordinates to the land base in real time. Levi Daniel possessed the skill of working with radio frequency devices and wireless communications. Regarding hardware, the circuits on board the boat must follow all safety practices to ensure that there are no accidents when the boat is in a body of water. Carter Ashby excels in circuit construction and component application, soldering, etc. Andrew Alley is also proficient in circuit design construction as well as having insight on power electronics.

As previously mentioned, a commercially available HSV is priced around $70,000. For this project, the price is greatly reduced due to the manual assembly of all systems, the ability to

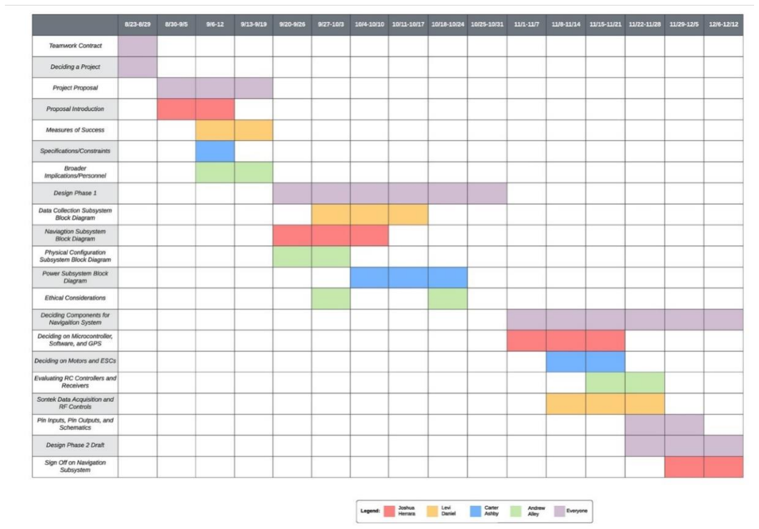
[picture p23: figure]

pay only for specific components, and the use of open-source software. The total cost of everything included in this project is approximately $2,300, as shown in Bill of Materials in Figure
24. This is well below the starting cost for a commercial unit.

IX. ETHICAL RESPONSIBILITIES
Throughout the duration of this project, the team always took into consideration economic and environmental ramifications regarding design as well as troubleshooting and testing. The Water Center has emphasized the importance of keeping this project cheaper than commercially available options. Not only would this save the Water Center money, but the project would allow for easier replicability for any communities interested in using this design to take their own hydrographic surveys. There were scenarios where the team needed to either purchase new components or replacements due to damage, so the team tried to maintain a balance of low-budget and overall performance when making these purchases.

In order to do effective experimental analysis, the boat needed to be tested in a controlled body of water because the T200 thrusters use the water to lubricate the plastic brushings as well as cool the motors. The team used Cane Creek Lake as the control environment due to it being within proximity to campus. Additionally, the Water Center requested that the boat be able to cover all of Cane Creek Lake in a single run. There was going to be no realistic scenario where the lake would be empty, so the team had to be cautious when doing testing. The team made sure to keep the boat away from any people to not cause any disturbances and prevent any injuries. Furthermore, the boat was always operated away from any wildlife, and if any animals were to get close, the user would drive the boat away and bring it back to land base.

X. LESSONS LEARNED
There were a few things that did not go as planned. These include issues regarding the circuitry of the battery monitoring system, programming the Raspberry Pi, receiving good GPS data, and the structural integrity of the hull.

The battery monitoring circuit had several problems to begin with. The first being that the output voltage of the balance plug on the LiPo batteries was not what we expected. We designed the battery monitoring circuit using differential amplifiers that were meant to output the difference between two pins on the balance plug. However, it was designed to find the difference between positive voltages, and 3 of the 5 pins on the balance plug output negative voltage. This required a redesign of the battery monitoring circuit, this time using quad op-amps since more voltage differences were required than previously thought. Another issue was found regarding the supply voltage of the quad op-amps. There was an issue with the way the op-amps were receiving power that made it difficult to output the correct voltages. The op-amps needed isolated power supplies to work properly. To solve this problem, we used a dual negative and positive supply circuit.

Programming the Raspberry Pi proved to be more difficult than we anticipated. The first issue was attempting to install Ubuntu Mate to the Pi. It took multiple attempts to determine that the problem was that the Pi was not able to output a display to the monitor we were using. For weeks, it was only possible

Figure 23: Gantt Chart

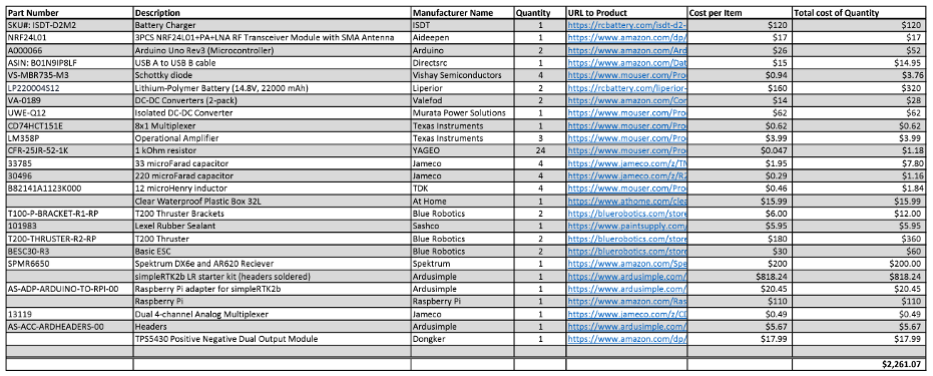
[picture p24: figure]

to display the Ubuntu Mate desktop through one monitor. This was solved by altering the configuration files of the Pi so that it could properly send an output through HDMI. Another issue with programming the Pi involved using C. It was intended to use C in ROS to create the code for the autonomous navigation. The issue with that was that the RTK (Real Time Kinematic) GPS could not interface properly with the Raspberry Pi using
C. After multiple attempts, we resorted to using Raspberry Pi OS instead of Ubuntu Mate to program the Pi. Also, we switched to using Python because it was found to be much simpler. We were unable to use ROS as well since it is not compatible with Raspberry Pi OS.

One of the significant issues that arose when trying to test the autonomous code, was that the Raspberry Pi would randomly receive invalid GPS data that could not be parsed or decoded. To solve this problem, the code was adjusted so that it would account for every case of invalid data. This included checking whether the data was encoded properly, whether there were enough data fields after it was parsed, and whether the latitude and longitude data was numeric.

The structural integrity of the hull was a big hindrance to the progress of the project. The hull was 3d printed by the TN Tech Water Center and coated with epoxy resin to waterproof the outside of the hull. This worked as planned, however, the inside of the hull was very porous and absorbed a lot of water when testing the boat. In the center of the middle piece of the hull, there is a hole for the River Surveyor M9 sonar sensor. While testing the boat, we did not have anything in the hole, so nothing was stopping the water from seeping into the 3d printed material. This caused the boat to nearly sink after a certain amount of testing. This limited any more tests that could be done with the autonomous navigation code until the inside of the hull was waterproofed.

A word of advice for future students would be to never assume anything works without testing it. It doesn’t matter if it is an extremely basic concept or design. It should be tested. The main thing that we would have done differently is to start the project using python and Raspberry Pi OS.

XI. CONCLUSION
The objective of this project was to design and construct an autonomous hydrographic surveying boat for the Tennessee Tech Water Center. The boat must transmit depth measurements to a land base in real time as well as switch between autonomous and manual control. Additionally, there needed to be an abort button/switch if the data being transmitted was inaccurate and obstacle avoidance for when the boat is in autonomous control.

The team was successful in creating a boat that can change between autonomous and manual control by flipping a switch on a remote controller. Additionally, the boat can accurately measure and transmit GPS and battery voltage data to a land base from approximately 600 meters away. The observed final operational time of the boat is 3 hours. The boat also successfully measures its current location with accuracy and precision in the centimeters by using simpleRTK2b GPS receivers, and a planned path can be created and implemented into the Raspberry Pi for autonomous navigation.

There have already been some discussions regarding potential ideas for future work and improvements to the autonomous hydrographic boat. The Water Center mentioned that the boat should be able to operate if the boat remains within the land base’s field of sight. The data, however, can only be successfully transmitted from approximately 600 meters from land base. The team speculates that this transmission range could be improved if the transmission bit rate was reduced on the Arduino Uno and nRF24L01+ RF modules. Additionally, the Python code could be improved by allowing users to drive a desired perimeter on a body of water and have the Raspberry Pi generate a set of parallel lines for the boat to traverse.

Figure 24: Bill of Materials

XII. INDIVIDUAL STATEMENTS

A. Joshua Herrera
For this project, I used the knowledge that I learned from Electrical Engineering Lab II, Circuits II, and Digital Systems Lab. From EE Lab II, I used what I learned about operational amplifiers to test and develop the battery monitoring circuits. Basic knowledge of circuitry assisted me in determining which resistors to use to create voltage dividers for testing the inputs to the Raspberry Pi. The knowledge that I learned in Circuits II allowed me to design the unused filters that were meant to convert PWM (Pulse Width Modulation) signals to DC voltages. Digital Systems Lab helped me when designing the analog multiplexer circuits. It allowed me to determine where pull-down resistors were needed and which voltages to use for logic 1 on the select lines.

The knowledge that I gained while working on this project was interfacing with a Raspberry Pi and learning to program in Python. Using the Raspberry Pi proved to be more difficult than I anticipated. Especially when online instructions made assumptions about pre-installed dependencies that were not pre-installed. I learned how to search for very specific errors every time they appeared when working with the Pi. I have also learned how to use Raspberry Pi add-ons and external devices such as the RTK GPS receiver. It used a serial connection which required several different dependencies to be installed.

Programming in Python was the biggest thing that I have learned while working on this project. I had avoided learning it at the beginning since it was a programming language that was unfamiliar to me. However, it proved to be a simple language to learn and became a valuable tool for the development of this project.

B. Andrew Alley
When deliberating on design choices and constructing the boat, I was able to implement my knowledge from ECE 4630, Power Electronics. This class proved beneficial to the project, for the practical batteries available in the market were outside of the operational voltage ranges of the Raspberry Pi, Arduino, and RC receiver. Power Electronics introduced the basic knowledge of DC-to-DC converters, which made the overall construction of the power system shorter than the team had anticipated. Additionally, ECE 3060, Electrical Engineering Lab 2, and ECE 3300, Electronics 1, provided insight regarding filter design for the buck converters as well as circuit design and soldering. Electrical Engineering also emphasized the importance of troubleshooting every component and node.

The main lesson I learned during my time working on this project is that real-life applications will almost never be equivalent to theoretical calculations. I was aware of this when starting the project; however, I did not realize how critical it was to be able to adapt quickly to these failures to stay on schedule. For example, when running LTSpice simulations on filtering a buck-boost converter, the designed schematic reduced the ripple voltage such that the output voltages of the connected buck and buck-boost converters would stay within the appropriate ranges for each device. The actual designed filter, on the contrary, reduced the ripple of the buck-boost to approximately 1.2 V, which was significantly larger than predicted in the LTSpice schematic. This required the team to quickly explore other options for powering the components in order to meet a desired deadline. This happened throughout the entirety of the project, but the team was able to change plans without negatively affecting overall performance. When working on engineering projects, it is important to have a plan with a strong foundation when in the design phase. Engineers must also understand that these plans may not be effective in the construction process and need to be able to quickly adapt when these likely scenarios occur and still be able to present a project by the final deadline.

C. Levi Daniel
Knowledge and experience gained in the signals and telecommunications courses provided me with a foundation to build on when I was researching and designing subsystems for this project that involved radio frequency communication and GPS. Also, knowledge gained in courses related to the communication of digital systems helped me to grasp how to design a system using serial communication between two or more components. Knowledge from circuit analysis and electronics courses was used to analyze circuit schematics and troubleshoot designs. Knowledge from my computer science courses was useful when programming microcontrollers and reading and implementing other algorithms.

I have learned a lot over the course of this project. A lot of the knowledge I have gained has either been built on a foundation of already established knowledge or has reinforced an area with additional learning or experience. Knowledge gained in this way is hard to measure and is easy to overlook when looking back. Other areas of learning where I learned or improved a skill or uncovered a new topic area are easier to recall. To name a few, I learned how to analyze a radio frequency connection using Link Budget Analysis. I used this to analyze and confirm the designs for the data transmission subsystem. I learned a lot about serial communication protocols and their differences, specifically SPI protocol. This was useful when designing the data transmission subsystem and the interface with the data acquisition subsystem. I also learned a lot about best practices when testing and troubleshooting a prototype. This was learned by experience when working with the developed prototype. And finally, I learned a lot about working with a team through the various stages of the engineering process. I learned better, more efficient ways to communicate and share ideas, and I learned how to handle various unique circumstances one might encounter in a team of unique engineers.

D. Carter Ashby
I found that my experience in Electrical Engineering Labs provided help in designing and building circuits for specific tasks in the project. More importantly, I was able to troubleshoot problematic circuits and fix unexpected issues, which I had developed the skills to do while building and testing circuits in our lab courses. It was also helpful to have programming knowledge and experience, especially when working to code the Arduino boards. Basic knowledge of electrical components, how they behave and interact in conjunction with other circuits, power performance, and other general electrical topics were all used and necessary to contribute to a project focused on autonomy.

I learned a lot about the implementation of specific ICs. Educational courses provide only the overview of a working device or circuit, and often require overlooking specific applications or functionality. I read through many device datasheets to understand the pinouts, composition, features, specifications, and functionality of several ICs or circuit boards in order to properly implement them into our systems. This is very important to the project as we had a few issues where systems did not work properly because the pre-built circuits we were using were not integrated correctly. It quickly became clear that we should learn every detail of the ICs before trying to use them in our applications.

References

[1] “FAQs: Spektrum - the leader in spread spectrum technology,” Spektrumrc.com. [Online]. Available: https://www.spektrumrc.com/Support/FAQs.aspx. [Accessed: 26-Jan-2022].
[2] “DX6e 6CH Transmitter Only,” Spektrumrc.com. [Online]. Available:
https://www.spektrumrc.com/Products/Default.aspx?ProdId=S PMR6650. [Accessed: 26-Jan-2022].
[3] “T200 thruster,” Blue Robotics. [Online]. Available: https://bluerobotics.com/store/thrusters/t100-t200-thrusters/t200-thruster-r2-rp/. [Accessed: 26-Jan-2022].
[4] “Blue robotics,” Blue Robotics. [Online]. Available: https://www.bluerobotics.com/store/thrusters/speed-controllers/besc30-r3/. [Accessed: 26-Jan-2022].
[5] “Raspberry pi GPIO Pinout,” Pinout.xyz. [Online]. Available: https://pinout.xyz/. [Accessed: 26-Jan-2022].
[6] “simpleRTK2B Long Range Starter Kit IP67, based on u-blox ZED-F9P,” ArduSimple, 10-Nov-2018. [Online].

Available: https://www.ardusimple.com/product/simplertk2b-starter-kit-lr-ip65/. [Accessed: 26-Jan-2022].

[7] “CD4051BC • CD4052BC • CD4053BC single 8-channel analog multiplexer/demultiplexer • dual 4-channel analog multiplexer/demultiplexer • triple 2-channel analog multiplexer/demultiplexer,” Jameco.com, 2000. [Online]. Available:
https://www.jameco.com/Jameco/Products/ProdDS/13119.pdf. [Accessed: 26-Jan-2022].
[8] “Raspberry Pi adapter for simpleRTK,” ArduSimple, 24-May-2019. [Online]. Available: https://www.ardusimple.com/product/raspberry-adapter-for-simplertk2b/. [Accessed: 26-Jan-2022].
[9] “Lithium-ion battery (14.8V, 15.6Ah),” Blue Robotics. [Online]. Available: https://bluerobotics.com/store/comm-control-power/powersupplies-batteries/battery-li-4s-15-6ah/. [Accessed: 26-Jan-2022].
[10] “5V 6A power supply,” Blue Robotics. [Online]. Available: https://bluerobotics.com/store/comm-control-power/elec-packages/bec-5v6a-r1/. [Accessed: 26-Jan-2022].
[11] “Raspberry Pi documentation - Raspberry Pi hardware,” Raspberrypi.com. [Online]. Available: https://www.raspberrypi.com/documentation/computers/raspb erry-pi.html. [Accessed: 26-Jan-2022].
[12] “CEE-USV,” CEE Hydrosystems. [Online]. Available: https://ceehydrosystems.com/products/unmanned-survey-vessels/cee-usv/. [Accessed: 20-Sep-2021].
[13] Acta.uni-obuda.hu. 2022. [online] Available at: <http://acta.uni-obuda.hu/Horvath_Pozna_Precup_81.pdf> [Accessed 3 May 2022].

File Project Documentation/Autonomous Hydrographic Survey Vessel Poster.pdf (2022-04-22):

# Autonomous Hydrographic Survey Boat


Introduction:
Hydrography is the science of surveying and charting bodies of water. Hydrographic surveying is important in the field of civil engineering, for groups must know the layout of a body of water before starting projects like dredging, diverting water sources, building docks, etc.
The team collaborated with the Tennessee Tech
Water | Center | to | create | an | autonomous
hydrographic surveying boat that can measure and map the depth of bodies of water and send the acquired data to an on-site technician in real time. This type of survey is conducted by navigating the boat back and forth across the body of water. Performing this task manually is labor-intensive and prone to error. Autonomous control eases the role of the technician while accomplishing the task more efficiently and accurately.

Team Members: Andrew Alley, Carter Ashby, Levi Daniel, & Joshua Herrera Faculty Advisor: Mr. Jesse Roberts


Future Work:
We have designed the boat to travel to certain desired points whose coordinates are listed on the Raspberry Pi. This Python code can be used as a base for a program that can generate a set of equidistant parallel lines across a body of water for the autonomous boat to travel. Future teams can work to integrate the current systems with the Sontek M9 HydroSurveyor sonar system provided by the Water Center to transmit and map recorded hydrographic measurements.

Acknowledgements:
We would like to thank Mr. Roberts for his guidance throughout our time working on this project. Additionally, we would like to thank Dr. Kalyanapu of the Civil and Environmental Engineering Department and the Water Center for funding this project.

From Left: Joshua Herrera, Andrew Alley, Levi Daniel, & Carter Ashby


Autonomous Boat Prototype


System Layout

Specifications:
- Design should be easily replicable for any group interested in using this project to take their own hydrographic measurements
- Successfully measure the entirety of Cane Creek Lake (56 acres) in one test run
- Travel at a speed of 3-5 ft/s to ensure accurate sonar data measurements
- Transmit hydrographic measurements, GPS location, and battery voltage levels from the boat to a land base in real time
- Can switch between manual and autonomous control

Experimental Analysis Results:


Data Transmission Samples vs Distance from Base Station


GPS Points Implemented into the Raspberry Pi for Autonomous Control

Final Product:

- The autonomous navigation algorithm is executed by a Raspberry Pi 4B
- RTK GPS data is used by the autonomous algorithm
- Wireless transmissions of GPS data and battery status to the base station are accomplished with a pair of Arduino Uno’s and RF modules over a maximum distance of 600 m
- The user can manually navigate the boat using a handheld RC and can switch control modes with a toggle switch
- LiPo batteries provide a lifetime of about 3 hours of
GPS Accuracy Experimentation

continuous testing

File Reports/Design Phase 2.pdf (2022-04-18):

# Autonomous Hydrographic Survey Vessel

Andrew Alley
Department of Electrical
Engineering
Tennessee Tech University
Cookeville, TN
atalley42@tntech.edu

Carter Ashby
Department of Electrical
Engineering
Tennessee Tech University
Cookeville, TN
cashby42@tntech.edu

Levi Daniel
Department of Electrical
Engineering
Tennessee Tech University
Cookeville, TN
lbdaniel42@tntech.edu

Joshua Herrera
Department of Electrical
Engineering
Tennessee Tech University
Cookeville, TN
jherrera42@tntech.edu
I. INTRODUCTION
The purpose of this project is to design and build a watercraft that autonomously navigates bodies of water to collect depth measurements with the use of sonar technology. These depth measurements will then be used to create a bathymetric map of the body of water for scientific study. The specifications that were provided for this project include the following. The boat must autonomously navigate the body of water. The boat should travel at 1-3ft/s. The weight of the boat should be light enough to be easily portable. The data from the sonar sensor should be streamed to a monitor to be viewed by the user. In case of an emergency, the boat will be able to abort data collection and return to the user.

II. SUBSYSTEMS
The following will be a description of each subsystem developed for the project along with their specifications followed by the detailed design of each subsystem.
A. Navigation System (Manual Control)
The manual control portion of the navigation system will assist in meeting the specifications that the boat will be autonomous and that the boat will have an abort operations function. For the boat to be able to autonomously navigate the body of water, the GPS coordinates of the perimeter of the lake must be measured. This process will require the user to manually drive the boat around the lake with a controller. The manual control system also needs to have programmable inputs for the abort function. In an emergency the user will press a button on the manual controller that tells the boat to stop collecting sonar data and return to the user. The user will also be able to tell the boat when to start collecting perimeter data, when to switch to manual control, and when to begin autonomous navigation. These will be assigned to inputs on the remote controller by the user. These functions were determined to be necessary to improve autonomy or ease of use.

The components that will be used for this system include the Spektrum DX6E controller and the Spektrum AR620 receiver. The decision to use this controller and receiver is based on its available programmable switches and its ability to operate the current boat model that was built by the Water Center at TN Tech. This was observed when a test run was conducted with the current boat model on Cane Creek Lake. The Spektrum controller will allow the project to meet the specification that the boat will be able to collect bathymetric data, the boat will be autonomous, and the boat will have the ability to abort data collection in case of an emergency. For the boat to begin collecting bathymetric data, it will need to be driven manually around the perimeter of the lake so that GPS data for the lake can be recorded. To do this, the Spektrum controller and receiver will need to output a signal that is capable of controller the electronic speed controllers (ESCs) that control the motors of the boat. This was observed by test driving the current model of the boat which implemented the Spektrum controller and receiver as well as Blue Robotics Basic ESCs and Blue Robotics T200 brushless thrusters. These are the same ESCs and thrusters that will be implemented in the autonomous boat. The range for the receiver is listed as 2 kilometers [1]. This distance is suitable for the purposes of navigating Cane Creek Lake. The length of Cane Creek is just over half a mile and since the user must always be able to see the boat, it will be easy for the user to stay within range. This controller also has extra switches on it that can be programmed for desired functions [2]. These switches can be assigned to the receiver outputs which will connect to the Raspberry Pi 4 in the onboard navigation system. These will control the boat’s mode of operation.


Figure 1: RC controller and Receiver

B. Navigation System (Autonomy)
The autonomous portion of the navigation system will directly meet the specification that the boat will be autonomous. It will use a GPS device to record data for the perimeter of the body of water. A microcontroller will process this data and create a path for the boat to travel that is optimal for sonar data collection. The microcontroller will then send signals to the motors that control the thrust to steer the boat along the created path. Signals from the user will be sent to the microcontroller to adjust the boat’s mode of operation.

The autonomous navigation system will require two Blue Robotics T200 thrusters, two Blue Robotics Basic ESCs, a Raspberry Pi 4 B, a 4-channel analog multiplexer, a simpleRTK2b medium range kit, and an adapter to connect the simpleRTK2b to the Raspberry Pi 4 B.

The Blue Robotics T200 thrusters are currently what the Water Center has for an old model of the boat. The Blue Robotics T200 thruster will be able to meet the specification that the boat should move at 1-3ft/s. Using the CAD files for the hull of the boat, an estimate of the weight was calculated. The total volume of the hull was found to be 9,381 cm^3. To be safe with the calculation of the hull’s weight, the highest density 3D printed material was used which was 2.16g/cm^3. Multiplying these two values results in a total weight of 20.264kg. This equates to an estimated weight is 44.67lb. The total weight of the hull and other components turns out to be about 52.18 lb. The maximum thrust of the T200 motors is 11.6lb of force [3]. Assuming the boat will accelerate to the desired speed of 3 ft/s or 0.9144 m/s within 1 second, the acceleration will need to be 0.9144m/s/s. Using the equation F = m*a, the force needed to accelerate a mass of 52.18lbs or 23.67kg at a rate of 0.9144m/s/s would be 21.64 Newtons or 4.86lbf. This is well within the capabilities of the T200 motor.


Figure 2: T200 Thruster

The Blue Robotics ESCs will be able to control the motors since these ESCs are specifically designed to control T200 or T100 motors. These ESCs are what the Water Center is currently using for their model of the boat. Here is a performance chart that displays the thrust of the T200 motor with different operating voltages while using the Blue Robotics Basic ESC R3 [3]. From the chart the thrust is highly adjustable using the Basic ESC R3 and adjustments to the operating voltage.


Figure 3: T200 Thruster Performance Chart

Figure 4: Blue Robotics Basic ESC

The Raspberry Pi 4 is necessary to meet the specification that the boat will be autonomous. The Raspberry Pi 4 will have ROS installed and the appropriate drivers necessary to process the GPS data from the simpleRTK2b board. The Raspberry Pi 4 will be capable of controlling the ESCs based on the documentation for both components. There are designated pins on the Raspberry Pi that can produce a PWM signal which is the required input signal for the ESCs [4][5]. Also, the voltage output of a Raspberry Pi 4 is 3.3V which is within the 3.3V-5V range required for the operation of the ESC [4][5].


Figure 5: Raspberry Pi 4 B

The simpleRTK2b long range kit will allow the project to meet the specification that the boat will collect bathymetric data and that the boat will be autonomous. This kit will allow the Raspberry Pi to know its latitude and longitude to within a few centimeters [6]. The boat will be driven around the perimeter of the lake before the sonar data collection begins. The GPS data for the perimeter of the lake will be processed by an ROS program in the Raspberry Pi to create a path that the boat will travel while it is collecting bathymetric data. Centimeter level accuracy is necessary to produce sufficient data to create bathymetric maps. The simpleRTK2b LR kit will be able to communicate NMEA protocol data messages that contain the


GPS coordinates [6]. This kit provides two simpleRTK2b boards. They will be set up in a “base and rover” configuration in which one board will be on the boat and one will be in a fixed position with a clear view of the sky. This allows the position of the boat to be calculated to within a few centimeters. This is necessary for the generated path to be optimal for sonar data collection. The GPS data is transferred between the boards using two antennas and two XBee radio modules [6]. The range of this kit is 10 km which exceeds any limitation set by the controller or other systems [6].


Figure 7: SimpleRTK2b Long Range Kit

The 4-channel mux will assist in meeting the specification that the boat will have an abort function. In case of an emergency, the user will flip a switch on the Spektrum RC controller. This will send a signal to the Raspberry Pi which will toggle one of the select lines on the mux [7]. The output of the mux will switch from the Raspberry Pi's motor control signal to the RC receiver's motor control signal.

Figure 8: 4-channel analog mux

The simpleRTK2b adapter for the Raspberry Pi 4 will be used for its intended use case which is to connect a Raspberry Pi 4 to a simpleRTK2b board [8].

Figure 6: Navigation Subsystem Full Schematic


Figure 9: simpleRTK2b Raspberry Pi Adapter

BILL OF MATERIALS

Qty | Part | Total Price
2 | Blue Robotics T200 Thrusters | $360
2 | Blue Robotics Basic ESCs | $60
1 | Dual 4-channel Analog Mux (10 Pack) | $13.98
1 | SimpleRTK2b LR Kit (Headers Soldered) | $818.24
1 | Raspberry Pi SimpleRTK2b Adapter | $20.45
1 | Raspberry Pi 4 B | $110
1 | Spektrum DX6E Transmitter and AR620 Receiver | $200
| Total | $1582.67
C. Data Acquisition and Transmission System
The objective of the Tennessee Tech Water Center is to collect accurate and complete bathymetric data for a body of water. This objective creates important specifications for the design of the survey vessel’s data acquisition subsystem. The Tennessee Tech Water Center has expressed that the boat must be able to collect measurements completely and accurately for Cane Creek Lake in Cookeville, TN. Cane Creek Lake is a 56-acre body of water (current depth measurements were inaccessible). An additional objective set by the Water Center is to view the collected data in real time to ensure that the boat is obtaining accurate and precise measurements. The data acquisition and transmission subsystem will be designed to meet these specifications.

The data acquisition and transmission system includes the sonar system and a data transmission board. The sonar system will have serial connections to the data transmission board and any other data transmission component that is recommended by the sonar manufacturer or desired by the user. For example, in the current design, the SonTek M9 sonar is being used, and it is connected to the data transmission board and the SonTek Power and Communication Module (PCM). The transmission board consists of a microcontroller that will connect to the sonar sensors serial output. In addition, the microcontroller will have a serial connection to the USB port of the navigation system’s simpleRTK2B module and will receive GPS data collected by this module. The microcontroller will then use an RF transceiver to transmit the collected data. Figure 7 shows the schematic for the onboard data subsystem.

The SonTek M9 Hydrosurveyor sonar sensor will be used to collect the water depth measurements. These measurements will be transferred to the SonTek PCM via a serial cable connection. The PCM has two battery compartments, each housing 8 AA batteries. These batteries supply voltage to the M9 to meet its 12-18 VDC requirement. In addition, the PCM uses multiplexing 2.4 GHz radio to communicate and send collected data to a USB radio dongle inserted in the user’s mobile computer at the on-land observation position.

It was necessary to consider the range of the SonTek radio communication link to confirm that the system met the given range specification. It was determined that the range of the remote controller’s optimal performance, about half a mile (~800 m), satisfied the specification and would be the limiting factor for all wireless communication onboard the boat. A 2 dBi gain external antenna will be connected to the PCM to improve the range. The PCM has three different options for transmit power: low (10 dBm), medium (19 dBm), and high (22 dBm). When using the external antenna and the high-power setting, the range is estimated to be around 1500 m. This well exceeds the limiting factor and will meet the range specification. The relevant analysis of the M9, the PCM, and the discussed radio communication has been done by SonTek and the results can be seen in their documentation.


Figure 10: Data Subsystem (on boat)

The Arduino Uno was selected to be used as the data transmission board because of its ability to handle a serial input baud rate of 9600, the serial output baud rate of the SonTek sonar sensor. Additionally, the Uno can communicate using a Serial Peripheral Interface (SPI), making it compatible with the selected RF transceiver for data transmission. Using the SonTek direct connect communications cable, the serial output of the M9 and the microUSB connection on the simpleRTK2B GPS module will be connected to the USB-B port of the Arduino


Uno. This communications cable combines two serial inputs into one serial output. The validity of this approach is pending on more information from SonTek. However, the GPS module was confirmed to meet the specifications for a GPS compatible with the M9. The specifications were as follows:
- Data output rate between 1-10 Hz (10 Hz recommended)
- Baud rate set to 38400
- NMEA output sentences: GPGGA and GPVTG (if used for position) and/or GPHDT (if used for heading).

The nRF24L01+ PA LNA wireless transceiver module has been selected for the transmission of collected data. This module supports programmable output power and has low power consumption. Available output power levels include 0 dBm, -6 dBm, -12 dBm or -18 dBm, and the module only consumes around 12 mA during transmission at 0 dBm. All the parameters can be configured through an SPI. Thistype of interface uses the concept of Master and Slave. In this case the Arduino Uno will be the Master and the transceiver will be the Slave. Also, this version of the module uses an external antenna, a power amplifier, and a low-noise amplifier to increase the transmission range from 100 m to 1000 m, a distance that satisfies the range specification. The correct operation of the transceiver modules has been analytically tested by reviewing the functionally and intended purpose for each pin and confirming that the Arduino has the appropriate pins to satisfy the requirements. For example, pins 5,6, and 7 on the transceiver have unique role pertaining to the SPI, and pins 11, 12, and 13 on the Uno directly correspond to these roles.

After the data is transmitted, it will be received on land to be viewed by the user. This system will consist of a radio frequency receiver and a microcontroller. This system will mirror the transmission system in that it will use a Arduino Uno and a nRF24L01+ PA LNA wireless transceiver module in the same configuration. The schematic can be seen in Figure 8. The radio frequency receiver module will receive a message signal encoded with collected data and will decode the signal to extract the measurement data. The microcontroller will be used to control the radio frequency module that receives an encoded radio wave. Once it has been decoded, the microcontroller will transport the received measurement data to a connected computer via a USB-B to USB-A serial connection. In addition, the SonTek radio dongle will be connected to a USB port on the computer and will receive measurement data collected by the M9 and transmitted from the PCM.


Figure 12: Data Subsystem (land)

Figure 11: Data Acquisition and Transmission System Full Schematic

BILL OF MATERIALS

Qty | Part | Total Price
2 | Arduino Uno Rev3 | $41.96
1 | NRF24L01+PA+LNA RF Transceiver Module with SMA Antenna 2.4 GHz + NRF24L01 8 Pin Socket Breakout Adapters Compatible (3 pcs each) | $29.18
1 | SonTek M9 Hydrosurveyor | Purchased
1 | SonTek PCM | Purchased
1 | SonTek 2 dBi gain antenna | Purchased
1 | SonTek communications cable | Purchased
1 | SonTek USB Radio dongle | Purchased
| Total | $71.14
D. Power System
A single battery will provide power for each system on the vessel, and the appropriate power will be distributed through a power distribution circuit [9]. The initial design included a power bus which will distribute power to the data acquisition system, the propulsion system, the navigation system, and the transmission system. However, the number of connections at the battery terminals can be reduced to three, so power will be distributed through two Blue Robotics DC-DC converters and the Raspberry Pi. The Raspberry Pi will receive power from the battery through a Blue Robotics converter and then provide power to the multiplexers and the GPS device through its own pins.

The Electronic Speed Controllers are the only two components that will be powered directly from the battery. The ESCs require 12-16 V for optimal operation. The device used to collect data from the SonTek M9 sonar device is the SonTek Power Communications Module, which requires 6 V. This PCM has an internal power system that uses AA batteries, which will be supplied by the user. The PCM is also used as the power source for the M9.

Blue Robotics provides a converter circuit that is designed to step down the voltage from the same power supply used for the ESCs to supply 5 V for a Raspberry Pi or similar device. Each converter circuit has two terminals to connect to a 7-26 V input power supply, and 4 pin outputs to supply power to two devices [10]. Two converter circuits will be used, one to power the Raspberry Pi and the RC receiver, and one to power the Arduino board, all of which requires 5 V. The SimpleRTK2B GPS system requires 5 V and will be powered directly from a 5 V output pin on the Raspberry Pi, using an adapter which fits directly into all GPIO pins on the Raspberry Pi [8]. This adapter uses a 5 V pin to receive power, a 3.3 V pin to define logic values, and will block the other 5 V power pin. In this case, the Raspberry Pi will need to be powered from the USB-C connection. A USB cable will be adjusted to connect to the converter circuit output pins and plugged into the Raspberry Pi directly. The multiplexers require 3-15 V and will be powered directly from the available 3.3 V output pin on the Raspberry Pi. The land-based GPS also requires 5 V, and it will be supplied by the user’s on-site PC via a USB connection.

A microcontroller will keep track of the current power level of the onboard battery. If the boat is still in autonomous operation when the battery level begins to drop below a percentage that risks the boat being left inoperable in the water, the boat will automatically stop data collection and begin navigation back to the starting point. This issue was addressed by Team 1 during the presentation of Design Phase 1.

Additionally, there is a risk of components short circuiting into the water while the boat is in operation. According to the National Institute for Occupational Safety and Health (NIOSH), a current of 100mA is considered fatal; however, only 10mA is needed to cause paralysis in water. To rectify this problem, a breaker circuit will be built onto the power bus that will detect any fluctuations in the currents of each component. If there is any change due to a short, the breaker will trip which results in the boat powering off.

The battery that will be used on the boat is a 14.8 V, 15.6 Ah Lithium-ion battery provided by Blue Robotics. [9] This single battery is designed to power a Blue Robotics Remotely Operated Vehicle with six thrusters onboard for approximately 2 hours under normal use. Since the autonomous boat will have only two thrusters, the battery capacity is large enough to handle the load in addition to the small amount of power required for the computing electronics. The thrusters have a maximum current draw of 20 A at 14 V each, when operating at full throttle. The battery can meet those requirements, as it can provide a maximum continuous current draw of 60 A. The required thrust calculated to maintain the specified boat speed is 4.86 lbf or 2.20 kgf. The thrusters can provide this amount of force while drawing approximately 6 A at 14 V [3]. This can be assumed to be the average current required from a single thruster. The Raspberry Pi 4 B has a maximum current draw of 1.2 A, which includes any peripheral components that are connected and powered on [11]. The RC receiver, when the boat is operating in manual mode, will allow the thrusters to draw the same amount of current that they would draw operating in autonomous mode. Then the total average current draw of all systems during normal operation is approximately 13.2 A. The current draw may be more or less, depending on the throttle of the motors, data collection, and data transmission. The Blue Robotics battery has a capacity of 15.6 Amp-hours, which will provide approximately one hour and ten minutes of runtime under a current draw of 13.2 A.

BILL OF MATERIALS

Qty | Part | Total Price
2 | Blue Robotics 5V 6A Power Supply | $44.00
1 | Blue Robotics Lithium-ion Battery (14.8V, 15.6Ah) | $290.00
| Total | $332.00


E. Boat Hull
The hull of the autonomous boat is provided by the Tennessee Tech Water Center. The hull is a trimaran, which is a multihull boat that comprises a main hull and two smaller outrigger hulls which are attached to the main hull with lateral beams. The main hull is approximately 5 feet in length and will have a hole in the center which will hold the SonTek in place when running trials. The outrigger hulls will be approximately 3 feet in length, and the CAD files will be displayed below. Based on the density of the filament used and an approximation of the hull’s volume, it is estimated that the weight of the hull will be 45 pounds. The following pictures display the CAD models that have been provided to us.


Figure 14: Side Piece of the Hull


Figure 15: SonTek Sensor Middle Piece

Figure 13: Power Subsystem Full Schematic


COMPLETE BILL OF MATERIALS

Qty | Part | Total Price
2 | Arduino Uno Rev3 | $41.96
1 | NRF24L01+PA+LNA RF Transceiver Module with SMA Antenna 2.4 GHz + NRF24L01 8 Pin Socket Breakout Adapters Compatible (3 pcs each) | $29.18
1 | SonTek M9 Hydrosurveyor | Purchased
1 | SonTek PCM | Purchased
1 | SonTek 2 dBi gain antenna | Purchased
1 | SonTek communications cable | Purchased
1 | SonTek USB Radio dongle | Purchased
2 | Blue Robotics T200 Thrusters | $360
2 | Blue Robotics Basic ESCs | $60
1 | Dual 4-channel Analog Mux (10 Pack) | $13.98
1 | SimpleRTK2b LR Kit (Headers Soldered) | $818.24
1 | Raspberry Pi SimpleRTK2b Adapter | $20.45
1 | Raspberry Pi 4 B | $110

Figure 16: Full Schematic

1 | Spektrum DX6E Transmitter and AR620 Receiver | $200
2 | Blue Robotics 5V 6A Power Supply | $44.00
1 | Blue Robotics Lithium-ion Battery (14.8V, 15.6Ah) | $290.00
2 | Blue Robotics 5V 6A Power Supply | $44.00
| Total Price | $1985.81

References

[1] “FAQs: Spektrum - the leader in spread spectrum technology,” Spektrumrc.com. [Online]. Available: https://www.spektrumrc.com/Support/FAQs.aspx. [Accessed: 26-Jan-2022].
[2] “DX6e 6CH Transmitter Only,” Spektrumrc.com. [Online]. Available:
https://www.spektrumrc.com/Products/Default.aspx?ProdId=S PMR6650. [Accessed: 26-Jan-2022].
[3] “T200 thruster,” Blue Robotics. [Online]. Available: https://bluerobotics.com/store/thrusters/t100-t200-thrusters/t200-thruster-r2-rp/. [Accessed: 26-Jan-2022].
[4] “Blue robotics,” Blue Robotics. [Online]. Available: https://www.bluerobotics.com/store/thrusters/speed-controllers/besc30-r3/. [Accessed: 26-Jan-2022].
[5] “Raspberry pi GPIO Pinout,” Pinout.xyz. [Online]. Available: https://pinout.xyz/. [Accessed: 26-Jan-2022].
[6] “simpleRTK2B Long Range Starter Kit IP67, based on u-blox ZED-F9P,” ArduSimple, 10-Nov-2018. [Online]. Available: https://www.ardusimple.com/product/simplertk2b-starter-kit-lr-ip65/. [Accessed: 26-Jan-2022].
[7] “CD4051BC • CD4052BC • CD4053BC single 8-channel analog multiplexer/demultiplexer • dual 4-channel analog multiplexer/demultiplexer • triple 2-channel analog multiplexer/demultiplexer,” Jameco.com, 2000. [Online]. Available:
https://www.jameco.com/Jameco/Products/ProdDS/13119.pdf. [Accessed: 26-Jan-2022].
[8] “Raspberry Pi adapter for simpleRTK,” ArduSimple, 24-May-2019. [Online]. Available: https://www.ardusimple.com/product/raspberry-adapter-for-simplertk2b/. [Accessed: 26-Jan-2022].
[9] “Lithium-ion battery (14.8V, 15.6Ah),” Blue Robotics. [Online]. Available: https://bluerobotics.com/store/comm-control-power/powersupplies-batteries/battery-li-4s-15-6ah/. [Accessed: 26-Jan-2022].
[10] “5V 6A power supply,” Blue Robotics. [Online]. Available: https://bluerobotics.com/store/comm-control-power/elec-packages/bec-5v6a-r1/. [Accessed: 26-Jan-2022].
[11] “Raspberry Pi documentation - Raspberry Pi
hardware,” Raspberrypi.com. [Online]. Available: https://www.raspberrypi.com/documentation/computers/raspb erry-pi.html. [Accessed: 26-Jan-2022].

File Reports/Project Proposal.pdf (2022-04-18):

I. INTRODUCTION

Bathymetry is the study and measurements of different bodies of water, such as lakes, rivers, oceans, etc. These analyses are crucial for determining the shape of the water body. Furthermore, data obtained from bathymetry can be used to monitor the effects of climate change, beach erosion, and subsidence. The Tennessee Tech Water Center also uses bathymetry to create simulations to predict natural disasters and locations that are more susceptible to flooding. The Water Center currently has boats that take bathymetric projections that are remote-controlled; however, this technology is prone to human
error | and | lacks | efficiency | that | could | be
further improved by automation. There are currently autonomous vehicles that take bathymetric measurements accurately and precisely, but these solutions are at a significantly higher budget than set by the Water Center.
A. Understanding This Paper

The point of this paper is to present the problem that this project is aiming to solve. The goal of this project is to develop an autonomous machine that measures the depth of bodies of water. These measurements will then be used to create an accurate bathymetry map of the lake, river or pond that is being mapped. The rest of this paper will describe the science and engineering behind this project and the process by which this project will be completed.

II. FORMULATING THE PROBLEM

In this section, the main objective of the project will be discussed as well as the specifications and constraints that make this objective worth working towards. The current solutions that are available will also be mentioned.

A. Background

The objective of this project is to create an autonomous, self-driving boat that will take water depth measurements of a body of water. These measurements will then be used to create bathymetry maps for bodies of water such as lakes, rivers, and ponds such as the map shown in Figure 1. Bathymetric data has many uses in scientific research. For example, bathymetry maps can be used for the prediction of flood inundation [1]. These maps can help water managers to calculate and perform simulations on how water would flow in possible scenarios such as flooding or broken dams [2]. This data can then be used to create potential evacuation routes and emergency protocols if these scenarios were to happen.


Figure 1: Bathymetry Map of Lake Superior

Boats or watercraft that are used to collect bathymetric data are known as hydrographic survey vessels (HSV). Bathymetric data is collected with HSVs using multiple techniques. This includes using a rod or weighted line that is placed in the water [3]. The line would be cast into the water to measure the depth and the coordinates of that measurement would be recorded. This process can take several days depending on the size of the body of water. Even then the number of data points that are recorded is often too low to produce a useful bathymetric map [4]. For lakes that are exceptionally deep, measuring rods become useless. The usefulness of this method depends on the navigability of the body of water as well since shallow waters make it difficult to use a full-size boat. Another more efficient method is to use sonar technology. Sonar sensors can measure the depth of a body of water using sound pulses or pings. These pings are transmitted from the sensor and travel until they hit the bottom of the body of water. These sound pulse are then reflected back and received by the sonar sensor. The time between transmitting and receiving is then used to determine the depth of the water. Sonar sensors used for bathymetry can typically detect depths of hundreds of feet. HSVs can be equipped with sonar sensors that are capable of measuring much further depths than a measuring rod [3, 4]. These HSVs also use a GPS to

### Autonomous Hydrographic Survey Vessel

Carter Ashby, Andrew Alley, Joshua Herrera, Levi Daniel record the location that each measurement is made. The number of measurements that can be taken drastically increases as well [4]. These types of HSVs are rather large since they are commonly used for oceanic bathymetry as seen in Figure 2. This means that navigability is still an issue.


Figure 2: Oceanic Hydrographic Survey Vessel

There are remote controlled HSVs that are available for use as well. These are typically much smaller than a full-size boat since they are unmanned. However, since they are remote-controlled, there is still human error when collecting data measurements. The boats will often take multiple measurements of one spot due to a lack of precision from the person controlling the boat. Accurate measurements of bodies of water are then potentially skewed, which then requires the need for more data recording to be done. Doing so can become a waste of time and the boat’s battery life.
An automated boat, however, can be given a certain path without overlap and can ensure appropriate water depth measurements are taken without redundancy. While automated boats are available in the commercial market, the price for these boats can start at around $70,000. The project would have a significantly smaller budget if a team were to program the boat themselves. Furthermore, this would also make the software more accessible to organizations and/or communities who would be
potentially | interested | in | using | an | automated
boat to improve safety protocols which can help reduce property damage and casualties.
Since there can still be errors that are not detected by the HSV, there should be an operator observing the data collection at all times. To make sure that the data is accurate, it will be streamed in real-time to a tablet. This will minimize the amount of error that is made when collecting the bathymetric data of the body of water.
B. Specifications

The size of the boat must be small enough that one or two people can lift and carry it for use and storage. The boat must be large enough that it can maneuver easily in the water without being influenced too much by water current or wind and without being too slow or cumbersome.
The boat must be able to support enough weight that the control circuits, communication electronics and sensors can all fit into the boat without issue.
The boat must be able to travel at a fast enough speed for normal travel around the water body, but also able to travel slow enough during data collection to allow for minute adjustments for each data point.
The battery life for the motors and sensors must be long enough to complete small water bodies without needing to stop and recharge. In conjunction with data collection speed, the boat will need to have a long enough battery life and a fast enough data collection that a water body such as Cane Creek Lake can be captured in one attempt.
The boat must be able to send a live feed of data to the on-site technician for monitoring. There must also be an abort collection option available to the technician, in case the data being collected does not seem suitable in real-time.
The boat must be able to withstand slight weather problems, such as light rain or wind. The boat will not be in operation when weather is severe, but the technician is not required to be “comfortable.”
The construction, assembly, and parts of the boat must be cheaper altogether than commercially available options.
In order to communicate wirelessly with the on-site technician, the boat will use either Wi-Fi or radio signals, which are regulated by certain government standards.
C. Constraints

The minimum size of the boat must be 3 feet long and 2 feet wide. The maximum size of the boat must be 5 feet long and 3 feet wide.
The boat must be able to handle a payload between 10 and 20 pounds, including control hardware and sensors.
The boat must collect data at speeds between 1 and 3 feet per second.
The battery life of the boat must be at least 1 hour. A water body with an area of roughly 2 million square feet must be able to be completed in one attempt. The regulations that govern remote control radio signals require that the boat only be controlled via radio signals in the 26-28 MHz band and that power output from the transmitter be no more than 4 Watts. The radio signals used to control the boat must also only control the boat; they cannot be used to transmit data from the collection process [5].
The regulations that govern Wi-Fi signals require that Wi-Fi frequencies be restricted to 902-928 MHz, 2400-2483.5 MHz, or 5725 to 5875 MHz, as they are considered unlicensed wireless equipment
devices [6]. The transmitter is also required not to exceed a peak output power of 1 Watt, and the Effective Isotropic Radiated Power (EIRP) cannot exceed 4 Watts [7]. The EIRP is simply a combination of the output power and the antenna gain.
D. Survey of Solutions
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

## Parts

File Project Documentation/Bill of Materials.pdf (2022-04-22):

Part Number | Description | Manufacturer Name | Quantity | URL to Product | Cost per Item | Total cost of Quantity
SKU#: ISDT-D2M2 | Battery Charger | ISDT | 1 | https://rcbattery.com/isdt-d2-mark-2-200w-24a-ac-dual-channel-output-smart-balance-charger.html $120 | | $120
NRF24L01 | 3PCS NRF24L01+PA+LNA RF Transceiver Module with SMA Antenna | Aideepen | 1 | https://www.amazon.com/dp/B07ZGQ2X7Q/ref=sspa_dk_detail_0?spLa=ZW5jcnlwdGVkUXVhbGlmaWVyPUExRDFKV0tXQ0UzSlFLJmVuY3J5cHRlZElkPUEwNzU1MDg2QlhKWlZIUFNGOFVTJmVuY3J5cHRlZEFkSWQ9QTEwMzI3NDAzTVAyVFFIUFBIMURNJndpZGdldE5hbWU9c3BfZGV0YWlsMiZhY3Rpb249Y2xpY2tSZWRpcmVjdCZkb05vdExvZ0NsaWNrPXRydWU&th=1 $17 | | $17
A000066 | Arduino Uno Rev3 (Microcontroller) | Arduino | 2 | https://www.amazon.com/Arduino-A000066-ARDUINO-UNO-R3/dp/B008GRTSV6/ref=asc_df_B008GRTSV6/?tag=hyprod-20&linkCode=df0&hvadid=309751315916&hvpos=&hvnetw=g&hvrand=13907036111092615516&hvpone=&hvptwo=&hvqmt=&hvdev=c&hvdvcmdl=&hvlocint=&hvlocphy=1025954&hvtargid=pla-457497319401&psc=1&tag=&ref=&adgrpid=67183599252&hvpone=&hvptwo=&hvadid=309751315916&hvpos=&hvnetw=g&hvrand=13907036111092615516&hvqmt=&hvdev=c&hvdvcmdl=&hvlocint=&hvlocphy=1025954&hvtargid=pla-457497319401 $26 | | $52
ASIN: B01N9IP8LF | USB A to USB B cable | Directsrc | 1 | https://www.amazon.com/Data-Sync-Cable-Arduino-Microcontroller/dp/B01N9IP8LF $15 | | $14.95
VS-MBR735-M3 | Schottky diode | Vishay Semiconductors | 4 | https://www.mouser.com/ProductDetail/Vishay-Semiconductors/VS-MBR735-M3?qs=MLItCLRbWszul51%252BZa4J%2Fg%3D%3D&mgh=1&gclid=Cj0KCQiA3rKQBhCNARIsACUEW_Y8_ieBrvfcZrt82YFDA6hY8GZJyMcGuK3uDzB_R-3Xm3BbDC7aLQUaAoRQEALw_wcB $0.94 | | $3.76
LP220004S12 | Lithium-Polymer Battery (14.8V, 22000 mAh) | Liperior | 2 | https://rcbattery.com/liperior-22000mah-4s-12c-14-8v-lipo-battery-with-xt90-plug.html $160 | | $320
VA-0189 | DC-DC Converters (2-pack) | Valefod | 2 | https://www.amazon.com/Converter-1-25-36V-Voltage-Regulator-Display/dp/B085T73CSD/ref=sr_1_4?crid=29LYXC6Q9QS3H&keywords=buck+converter+5a&qid=1643862041&s=electronics&sprefix=buck+converter+5%2Celectronics%2C85&sr=1-4 $14 | | $28
UWE-Q12 | Isolated DC-DC Converter | Murata Power Solutions | 1 | https://www.mouser.com/ProductDetail/Murata-Power-Solutions/UWE-12-10-Q12PB-C?qs=sGAEpiMZZMsKEdP9slC0YXesACu0naazurpD67urIRM%3D $62 | | $62
CD74HCT151E | 8x1 Multiplexer | Texas Instruments | 1 | https://www.mouser.com/ProductDetail/Texas-Instruments/CD74HCT151E?qs=spW5eSrOWB6Rz3oKuCPHHQ%3D%3D&mgh=1&gclid=Cj0KCQiAjJOQBhCkARIsAEKMtO1SKSPmZhWCtrLzN6BYatLjcZWIYPjZcIGMgPF3ZNaXJYGQ9sIX0cwaAuTyEALw_wcB $0.62 | | $0.62
LM358P | Operational Amplifier | Texas Instruments | 3 | https://www.mouser.com/ProductDetail/Texas-Instruments/LM358P?qs=X1HXWTtiZ0QtOTT8%252BVnsyw%3D%3D&mgh=1&gclid=Cj0KCQiA0p2QBhDvARIsAACSOOPHLgqJCQ0ume93mizuOE0FOIYV3IMa-VgJD7a-y49PWQSSDLXKG80aAkX1EALw_wcB $3.99 | | $3.99
CFR-25JR-52-1K | 1 kOhm resistor | YAGEO | 24 | https://www.mouser.com/ProductDetail/YAGEO/CFR-25JR-52-1K?qs=sGAEpiMZZMtlubZbdhIBIG2rwDeDG2Hz0nFs2Ia3WF8= $0.047 | | $1.18
33785 | 33 microFarad capacitor | Jameco | 4 | https://www.jameco.com/z/TM33-25-Jameco-Valuepro-33uF-25-VOLT-TANTALUM-CAPACITOR_33785.html $1.95 | | $7.80
30496 | 220 microFarad capacitor | Jameco | 4 | https://www.jameco.com/z/R220-25-Jameco-Valuepro-220-uF-25-Volt-Radial-Capacitor_30496.html $0.29 | | $1.16
B82141A1123K000 | 12 microHenry inductor | TDK | 4 | https://www.mouser.com/ProductDetail/EPCOS-TDK/B82141A1123K000?qs=%2FsLciWRBLmCb9ti2vFWH1A%3D%3D $0.46 | | $1.84
| Clear Waterproof Plastic Box 32L | At Home | 1 | https://www.athome.com/clear-waterproof-storage-box-32l/124319743.html?utm_source=Google&utm_medium=Organic&utm_campaign=Free_Listings&utm_content=PLA_Enhanced_Free_Listings $15.99 | | $15.99
T100-P-BRACKET-R1-RP | T200 Thruster Brackets | Blue Robotics | 2 | https://bluerobotics.com/store/thrusters/t100-t200-thrusters/t100-p-bracket-r1/ $6.00 | | $12.00
101983 | Lexel Rubber Sealant | Sashco | 1 | https://www.paintsupply.com/product/caulk-foam-sealants/polymers-urethanes/advanced-polymer/5-5-oz-sashco-13013-clear-lexel-synthetic-rubber-sealant/?utm_source=google&utm_medium=surfaces&gclid=CjwKCAiAl-6PBhBCEiwAc2GOVO2BlcEoVrc-tLznnfEaFLM6xxw5LpMs8VjFnG8ctzQW_aXHaBt2sRoCwNsQAvD_BwE $5.95 | | $5.95
T200-THRUSTER-R2-RP | T200 Thruster | Blue Robotics | 2 | https://bluerobotics.com/store/thrusters/t100-t200-thrusters/t200-thruster-r2-rp/ $180 | | $360
BESC30-R3 | Basic ESC | Blue Robotics | 2 | https://bluerobotics.com/store/thrusters/speed-controllers/besc30-r3/ $30 | | $60
SPMR6650 | Spektrum DX6e and AR620 Reciever | Spektrum | 1 | https://www.amazon.com/Spektrum-6-Channel-Transmitter-Receiver-Telemetry/dp/B07N8ZPMJY/ref=sr_1_1_sspa?gclid=Cj0KCQiA-K2MBhC-ARIsAMtLKRvlk0kN3jLUXreXzaf5oE8_JRNXZJAKt7dclpJUxfEz9pTMIaPtdnoaAuZ1EALw_wcB&hvadid=557195307256&hvdev=c&hvlocphy=1025954&hvnetw=g&hvqmt=e&hvrand=2845816924598946000&hvtargid=kwd-45152166219&hydadcr=2111_13434996&keywords=spektrum+dx6e&qid=1636570526&sr=8-1-spons&psc=1&spLa=ZW5jcnlwdGVkUXVhbGlmaWVyPUEyTjg3WDM3Sjk2VDdVJmVuY3J5cHRlZElkPUEwOTc2NDI2MlVXRzc3TUdEWkc4OCZlbmNyeXB0ZWRBZElkPUEwMTk3ODgxN1RSMzgzQVI1MDJEJndpZGdldE5hbWU9c3BfYXRmJmFjdGlvbj1jbGlja1JlZGlyZWN0JmRvTm90TG9nQ2xpY2s9dHJ1ZQ== $200 | $200.00
| simpleRTK2b LR starter kit (headers soldered) | Ardusimple | 1 | https://www.ardusimple.com/product/simplertk2b-starter-kit-lr-ip65/ $818.24 | $818.24
AS-ADP-ARDUINO-TO-RPI-00 | Raspberry Pi adapter for simpleRTK2b | Ardusimple | 1 | https://www.ardusimple.com/product/raspberry-adapter-for-simplertk2b/ $20.45 | $20.45
| Raspberry Pi | Raspberry Pi | 1 | https://www.amazon.com/Raspberry-Model-2019-Quad-Bluetooth/dp/B07TC2BK1X/ref=asc_df_B07TC2BK1X/?tag=hyprod-20&linkCode=df0&hvadid=380145854123&hvpos=&hvnetw=g&hvrand=1979957359553226829&hvpone=&hvptwo=&hvqmt=&hvdev=c&hvdvcmdl=&hvlocint=&hvlocphy=1025954&hvtargid=pla-818643320764&psc=1&tag=&ref=&adgrpid=85982211068&hvpone=&hvptwo=&hvadid=380145854123&hvpos=&hvnetw=g&hvrand=1979957359553226829&hvqmt=&hvdev=c&hvdvcmdl=&hvlocint=&hvlocphy=1025954&hvtargid=pla-818643320764 $110 | $110
13119 | Dual 4-channel Analog Multiplexer | Jameco | 1 | https://www.jameco.com/z/CD4052B-Major-Brands-IC-CD4052-DUAL-4-CHANNEL-ANALOG-MULTIPLEXER_13119.html $0.49 | $0.49
AS-ACC-ARDHEADERS-00 | Headers | Ardusimple | 1 | https://www.ardusimple.com/product/headers-kit-not-soldered/ $5.67 | $5.67
| TPS5430 Positive Negative Dual Output Module | Dongker | 1 | https://www.amazon.com/dp/B081WWN3VJ?psc=1&ref=ppx_yo2ov_dt_b_product_details $17.99 | $17.99

$2,261.07

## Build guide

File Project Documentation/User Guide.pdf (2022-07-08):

## USER GUIDE

GPS Base Station Setup

1. Open u-center on a personal computer.
2. Connect one u-blox antenna to the base station via the female SMA port on the simpleRTK2b module.
3. Connect the dipole antenna to the base station via the female SMA port on the XBee module.
4. Connect a micro-USB connector to the accompanying port on the simpleRTK2b module labelled “POWER + GPS.”
5. Insert the USB connector of the micro-USB cable into an available USB port on the personal computer with the u-center software.
6. In u-center, under the “Connect serial port” option, select the corresponding COM port for the GPS device.
7. Wait for “Fix Mode” to display “TIME.” (~10 minutes)

Onboard Powerup

1. Connect each battery power plug to the female connectors on the power bus.
2. Connect each battery balance cable to the battery monitoring circuit. The red wires for each cable must be connected to pins [b13] and [h18], respectively.
3. Connect the other u-blox antenna to the rover station on the boat via the female SMA port on the simpleRTK2b module, facing the bottom of the boat.
4. Connect the other dipole antenna to the rover station via the female SMA port on the XBee module, facing the top of the boat.
5. Connect the USB-C cable to the accompanying port on the Raspberry Pi.
6. Power on the boat using the power switch.
7. Put the lid in place over the antenna on the Raspberry Pi GPS module, and attach a smaller dipole antenna to the Arduino module via the female SMA connector.
8. Fasten the lid by securing the clamps over the handles on each end of the lid, tucking any cables underneath the rim of the lid.

NOTE: The Raspberry Pi must be allowed to fully complete the bootup process (~2 minutes) before powering off the system.

Battery Monitor Setup

1. Open Arduino on a personal computer.
2. Connect the other small, dipole antenna to the base Arduino module via the female SMA connector.
3. Connect a USB-B connector to the accompanying port on the base Arduino.

4. Insert the USB-A connector of the USB cable into an available port on the personal computer with the Arduino software.
5. Under the Tools menu, select “Serial Monitor.”
6. Ensure the baud rate selected is identical to the baud rate of the transmitting Arduino (by default, 115200).

Switch to Autonomous Mode

1. Place the boat in water deep enough to allow the hull to settle into the water, bearing the full weight of the boat.
2. Ensure that Switch A on the controller is set to position 0 (Manual).
3. Power on the RC controller by pressing the power button in the center of the controller.
4. Hold the left throttle down until the controller is fully powered on.
5. A short tone of five beeps emitted by the ESCs on the boat indicate a connection between the controller and the motors.
6. Set Switch A on the controller to position 1 for Autonomous mode.

The boat is now operational. While the boat will always be operational in Manual mode, the boat will only begin running in Autonomous mode once the Raspberry Pi has finished the startup sequence and begins to implement the current program.

NOTE: Mode of operation is determined by Switch A:
position 0 = Manual; position 1 = Autonomous

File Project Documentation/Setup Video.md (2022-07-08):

# Setup Video Link: <br/>
https://drive.google.com/file/d/1U7a6jqmT3CKm41x2pFMPDlh_aL9Kb4Bw/view?usp=sharing

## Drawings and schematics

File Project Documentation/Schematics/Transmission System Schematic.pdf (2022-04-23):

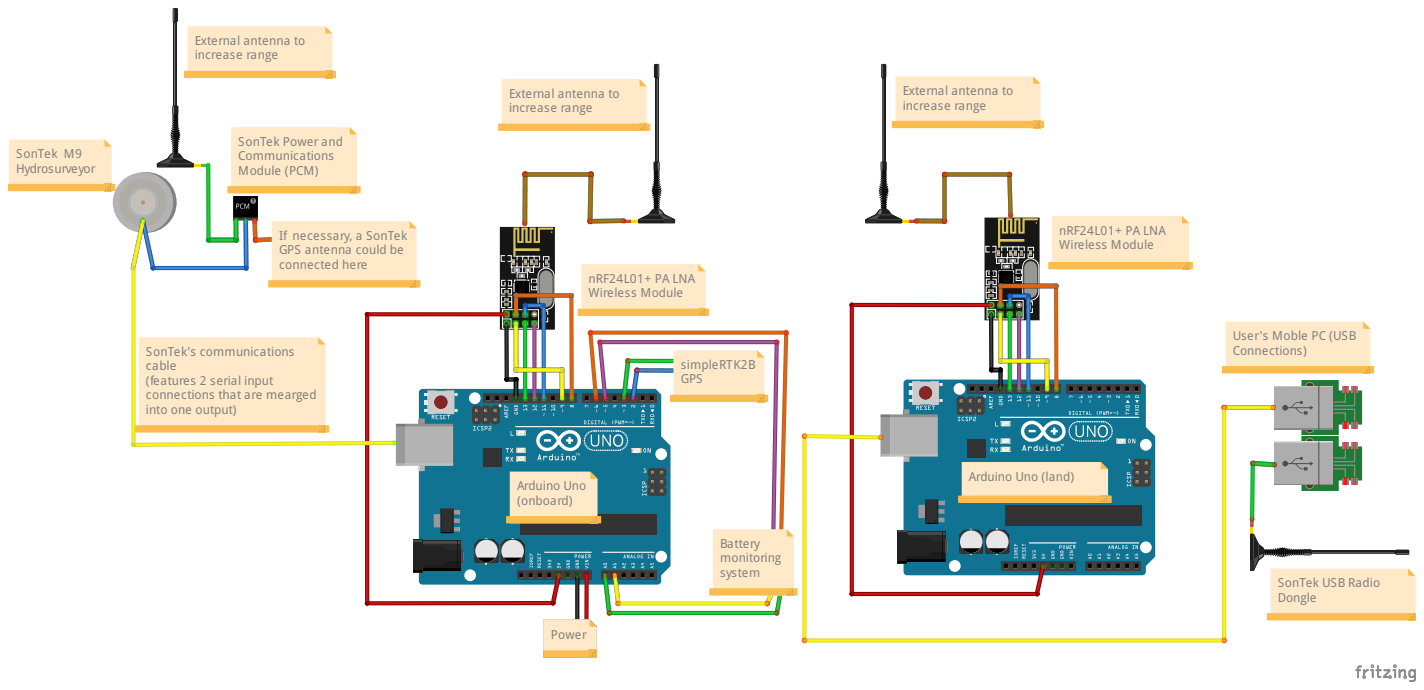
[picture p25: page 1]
nRF24L01+ PA LNA Wireless Module; SonTek M9 Hydrosurveyor; Arduino Uno (onboard); simpleRTK2B GPS; Power; Battery monitoring system

External antenna to
increase range

SonTek Power and
Communications
Module (PCM)

If necessary, a SonTek
GPS antenna could be
connected here

User's Moble PC (USB
Connections)

SonTek's communications
cable
(features 2 serial input
connections that are mearged
into one output)

Arduino Uno (land)

SonTek USB Radio
Dongle

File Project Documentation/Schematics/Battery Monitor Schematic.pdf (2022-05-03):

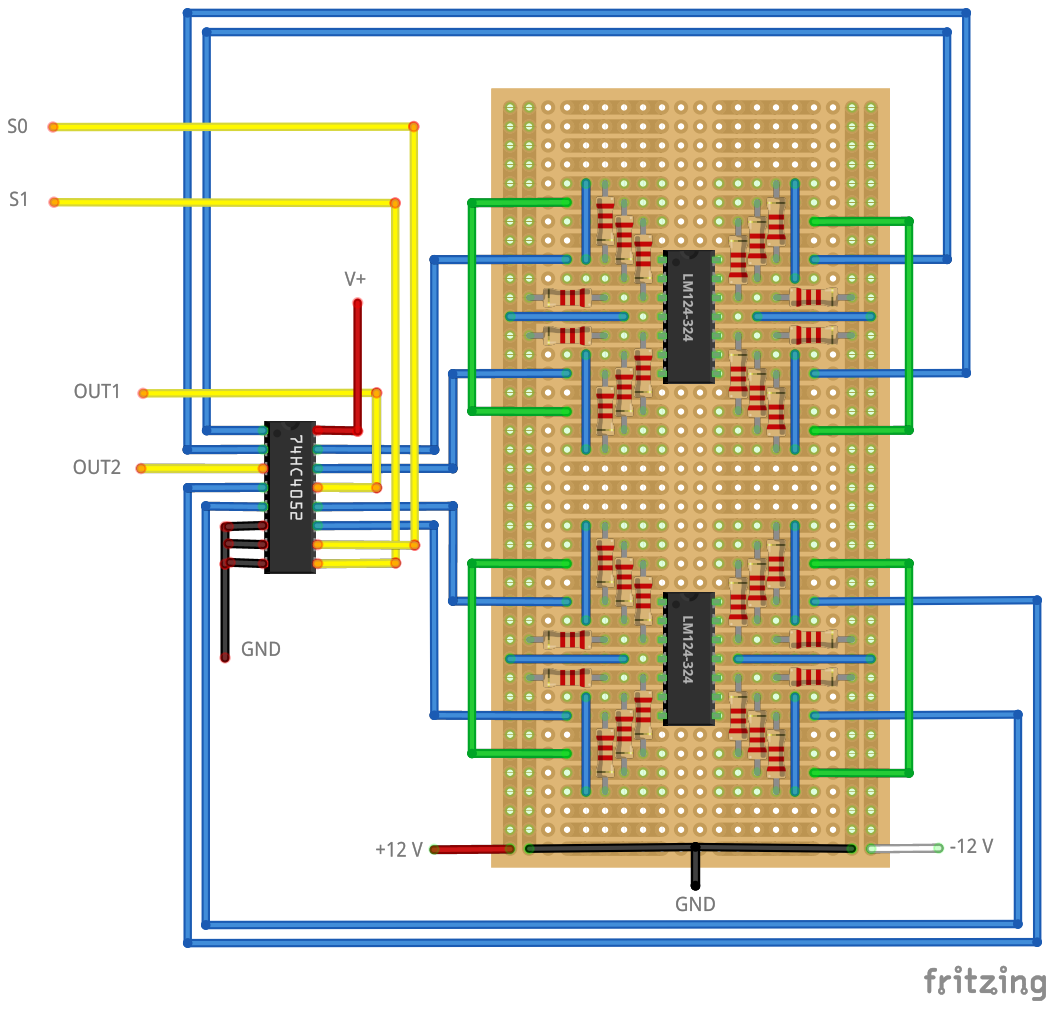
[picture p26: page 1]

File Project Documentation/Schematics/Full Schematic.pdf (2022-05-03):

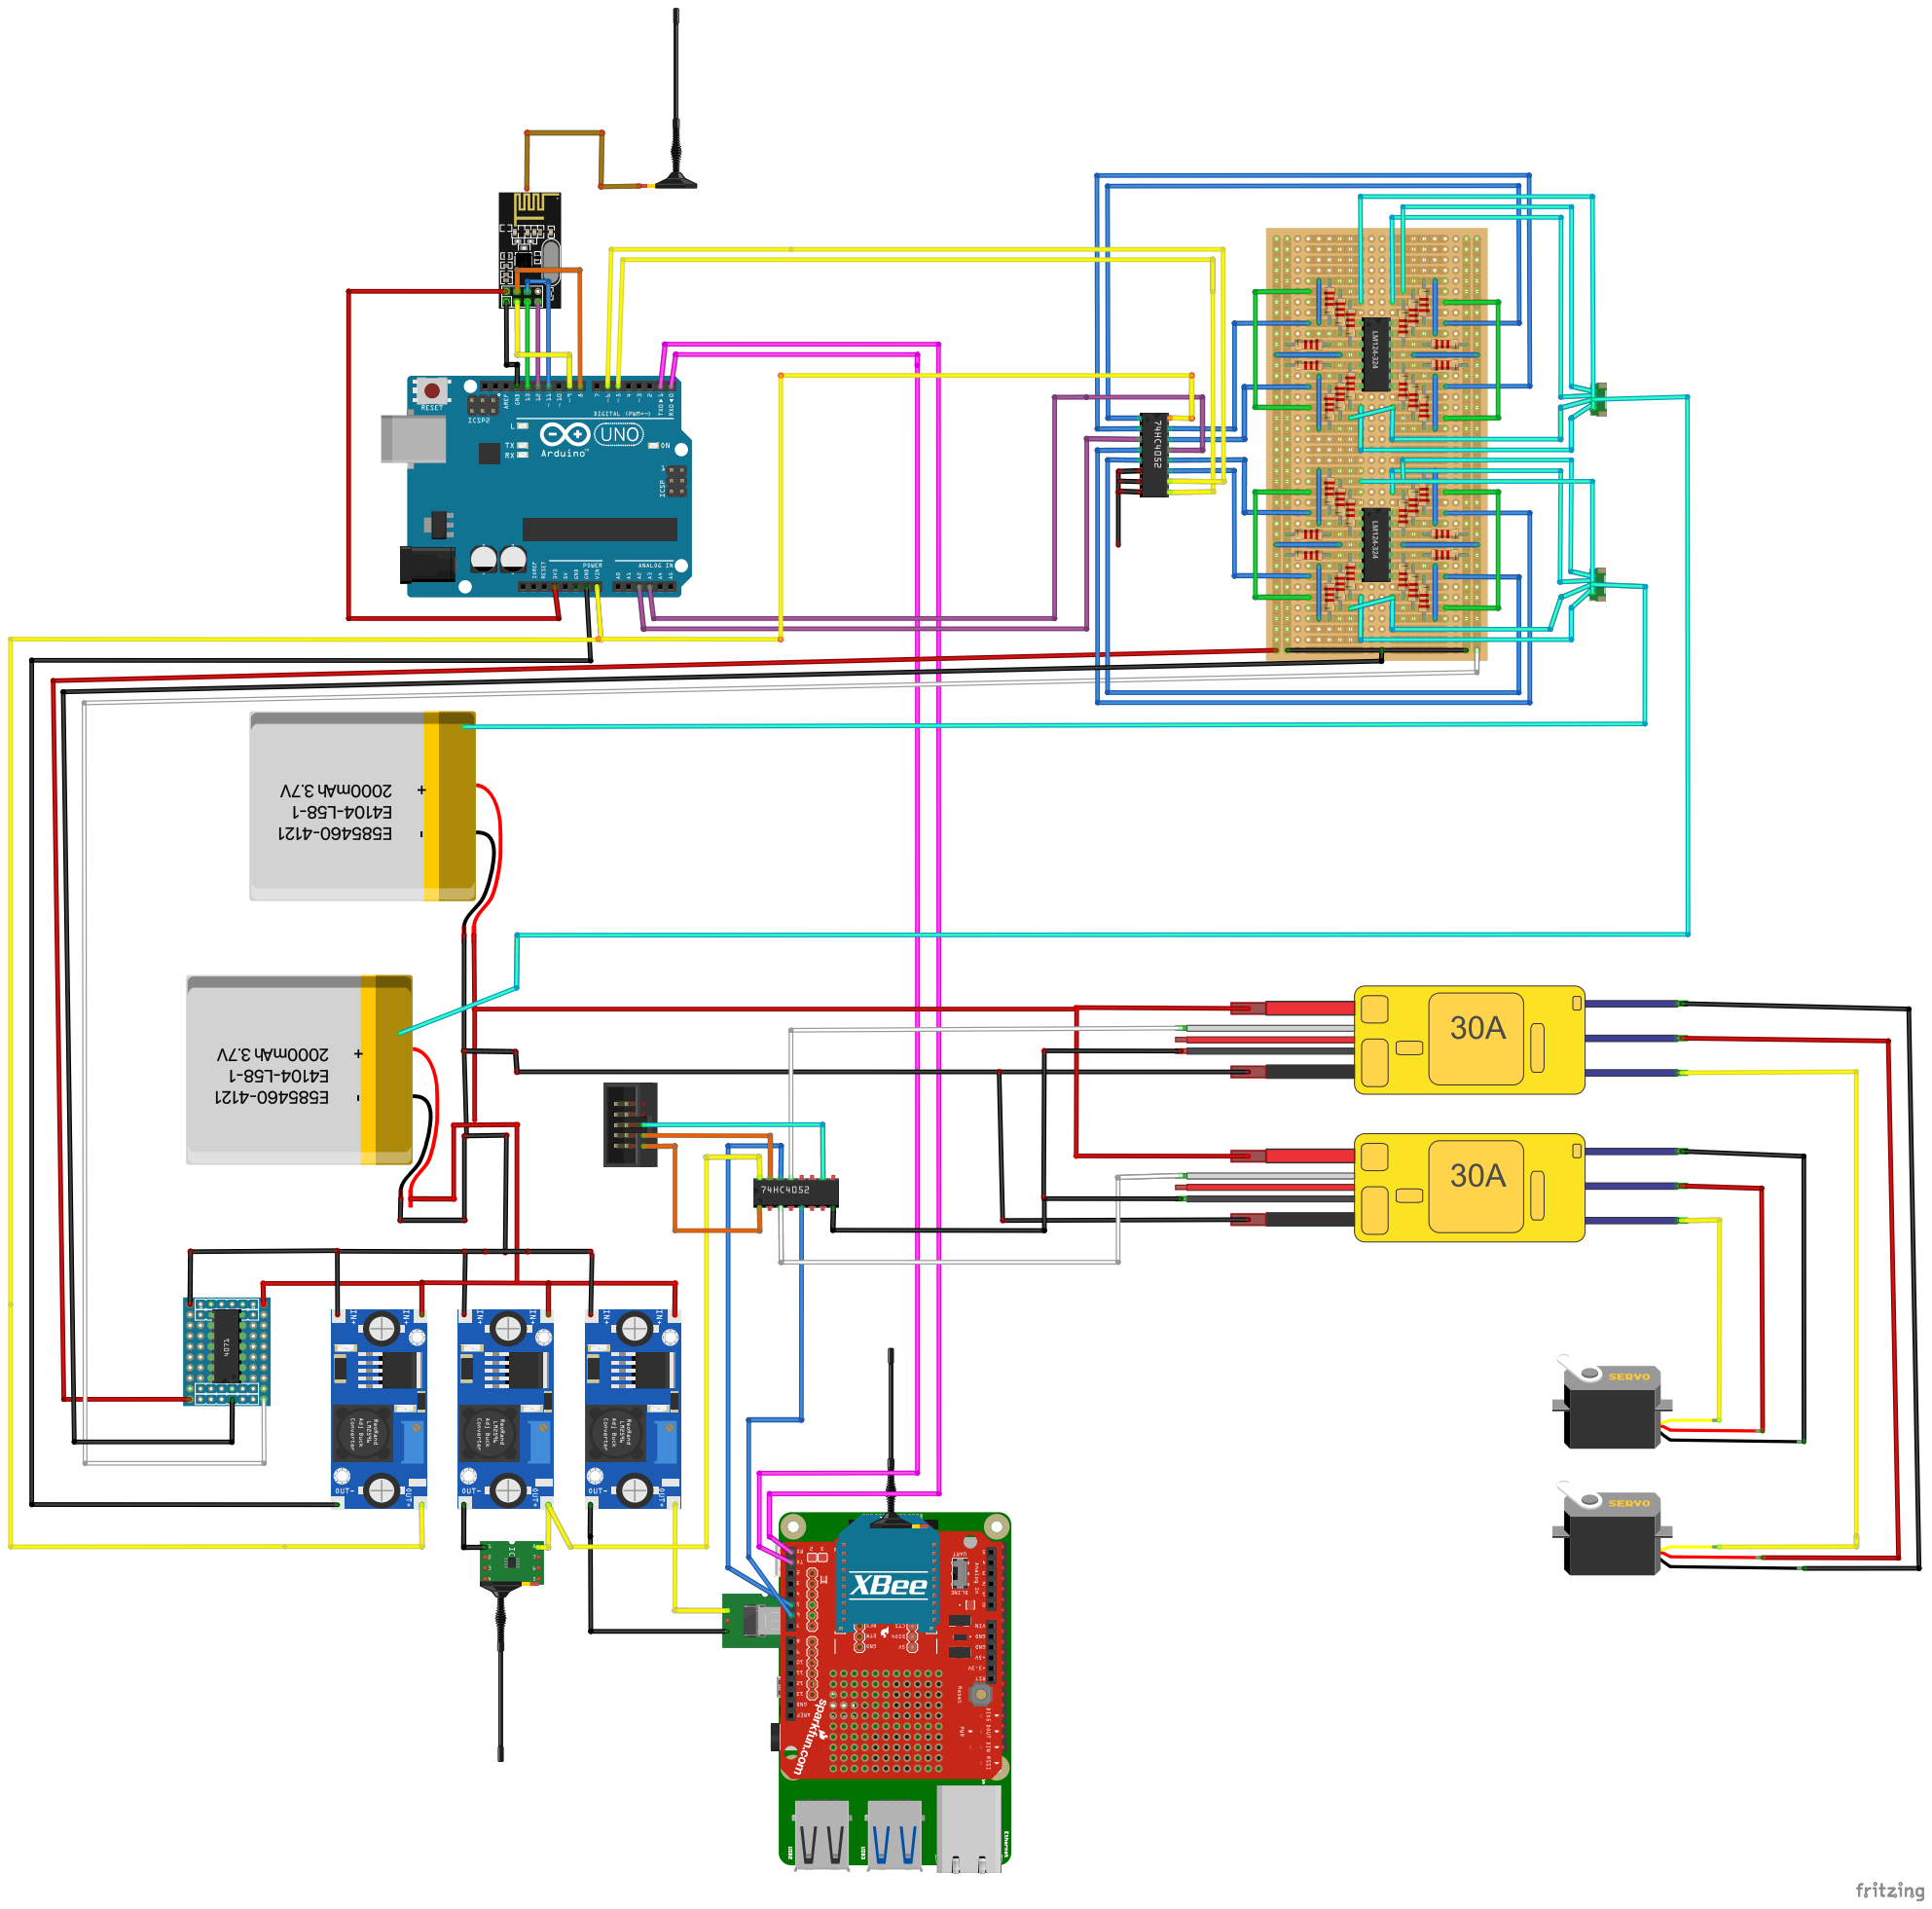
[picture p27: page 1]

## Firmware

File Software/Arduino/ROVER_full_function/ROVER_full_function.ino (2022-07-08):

// This might help solve the anti-static bag problem: https://www.youtube.com/watch?v=VOC2JRLQZh0
// Plenty of other methods can be found with a quick search of "fixing range of nRF24l01+ pa/lna module"

#include <SPI.h>
#include "printf.h"
#include "RF24.h"
#include <SoftwareSerial.h>

SoftwareSerial mySerial(2, 3); // RX, TX

// instantiate an object for the nRF24L01 transceiver
RF24 radio(9, 8); // using pin 9 for the CE pin, and pin 8 for the CSN pin

const byte address[6] = "00001";
char msg[90] = {0};
String battery_msg;
char battery_msg_char[32] = {0};

int SelectPin0 = 5;
int SelectPin1 = 6; // Pins used for mux select lines
int MeasuredCell1 = A0;
int MeasuredCell2 = A1; // Pin used to measure voltage from mux
float CellVoltage1 = 0;
float CellVoltage2 = 0;
float MinVoltage = 2.5; // Threshold for "dead" battery cell

void SelectLineOut(bool S0, bool S1) {
  digitalWrite(SelectPin0, S0);
  digitalWrite(SelectPin1, S1);
}

bool BatteryCheck() {
  // Cycles through select lines outputs 00,01,10,11
  for (int i = 0; i < 4; i++)
  {
    SelectLineOut(bitRead(i, 0), bitRead(i, 1));
    CellVoltage1 = analogRead(MeasuredCell1) * 5.07 / 1024.0; // Checks the voltage at both
    //delay(10);
    CellVoltage2 = analogRead(MeasuredCell2) * 5.07 / 1024.0; // cells for each select line output

    battery_msg = String(String(CellVoltage1, 2) + "  " + String(CellVoltage2, 2));
    if (i == 3) {
      battery_msg = String(String(CellVoltage1, 2) + "  " + String(CellVoltage2, 2) + "\n");
    }
    battery_msg.toCharArray(battery_msg_char, 32);
    //Serial.println(battery_msg_char);
    //Serial.println(strlen(battery_msg_char)+1);
    radio.write(&battery_msg_char, strlen(battery_msg_char) + 1);
    /*if(CellVoltage1 < MinVoltage)
      return true;
      if(CellVoltage2 < MinVoltage)
      return true;*/

  }
}

void setup() {

  // Battery Monitoring Pins
  pinMode(SelectPin0, OUTPUT);
  pinMode(SelectPin1, OUTPUT);
  pinMode(MeasuredCell1, INPUT);
  pinMode(MeasuredCell2, INPUT);

  Serial.begin(115200);

  mySerial.begin(115200);
  //mySerial.println("mySerial");
  //Serial.println("Serial");

  radio.begin();

  radio.setPALevel(RF24_PA_HIGH);  // RF24_PA_MAX is default.

  // set the TX address
  radio.openWritingPipe(address);

  // put radio in TX mode
  radio.stopListening();

}

void loop() {

  if (mySerial.available()) {
    for (int pos = 0; pos < 90; pos++)
    {
      msg[pos] = mySerial.read();
    }
    //Serial.println(msg);

    radio.write(msg, strlen(msg));
  }

  if (!mySerial.available()) {
    const char err[] = "NoData";
    radio.write(&err, sizeof(err));
    Serial.println(err);
  }
  else {
    radio.write(&msg, sizeof(msg));
  }

  BatteryCheck();
  //Serial.println();

  //delay(250);


}

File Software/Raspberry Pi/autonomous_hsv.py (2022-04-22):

import RPi.GPIO as GPIO
import time
import serial
import math
import stateplane

GPIO.setwarnings(False)
GPIO.setmode(GPIO.BCM)
GPIO.setup(10, GPIO.OUT)
GPIO.setup(9, GPIO.OUT)
GPIO.setup(11, GPIO.OUT)
GPIO.setup(22, GPIO.OUT)
GPIO.setup(27, GPIO.OUT)
#GPIO.setup(25, GPIO.IN)
#GPIO.setup(8, GPIO.IN)
#GPIO.setup(23, GPIO.IN)

countyfips = 47141

# Planned Path
lats = [36.160707, 36.1614368, 36.1621665, 36.1622055, 36.1614909, 36.1607763, 36.1608326, 36.1615364, 36.1622402, 36.1622748, 36.1615732, 36.1608716, 36.1609192, 36.1616014, 36.1622835, 36.1622878, 36.1616122, 36.1609365, 36.1609668, 36.1616187, 36.1622705, 36.1622878, 36.1616447, 36.1610015, 36.1610275, 36.1616663, 36.1623051, 36.1628855, 36.1619717, 36.1610578, 36.1610924, 36.1621622, 36.1632319, 36.1633186, 36.1622445, 36.1611704, 36.161231, 36.1622921, 36.1633532, 36.1634052, 36.1623441, 36.161283, 36.1613436, 36.1624134, 36.1634831, 36.1635178, 36.1624654, 36.1614129, 36.1614562, 36.162513, 36.1635697, 36.1635524, 36.1625303, 36.1615082, 36.1615602, 36.162565, 36.1635697, 36.1635697, 36.1626039, 36.1616381, 36.1616555, 36.1626343, 36.1636131, 36.163691, 36.1626906, 36.1616901, 36.1617161, 36.1627252, 36.1637343, 36.1638036, 36.1627815, 36.1617594, 36.1617378, 36.1628097, 36.1638816, 36.1639768, 36.1628768, 36.1617767, 36.16182, 36.1629201, 36.1640202, 36.1640981, 36.1629721, 36.161846, 36.1620539, 36.163102, 36.1641501, 36.1642454, 36.1632276, 36.1622098, 36.1623571, 36.1632406, 36.1641241, 36.1637949, 36.1631496, 36.1625043, 36.1626689, 36.163193, 36.163717, 36.1637083, 36.1631843, 36.1626603, 36.1626949, 36.16318, 36.163665, 36.1636564, 36.1631973, 36.1627382, 36.1627036, 36.1631757, 36.1636477, 36.1636304, 36.1631497, 36.1626689, 36.1626862, 36.163167, 36.1636477, 36.1636564, 36.1631627, 36.1626689, 36.1627122, 36.163206, 36.1636997, 36.1636997, 36.16318, 36.1626603, 36.1626603, 36.1631973, 36.1637343, 36.1637516, 36.163167, 36.1625823, 36.1626862, 36.1632103, 36.1637343, 36.1637776, 36.1633272, 36.1628768]
lons = [-85.5473399, -85.5476269, -85.5479139, -85.5477637, -85.5474821, -85.5472004, -85.5470556, -85.5473346, -85.5476135, -85.5474526, -85.5471763, -85.5469, -85.5467552, -85.5470261, -85.547297, -85.5471307, -85.5468706, -85.5466104, -85.5464655, -85.546723, -85.5469805, -85.5468303, -85.5465701, -85.5463099, -85.5461758, -85.5464172, -85.5466586, -85.5467176, -85.5463609, -85.5460042, -85.5458379, -85.5462617, -85.5466855, -85.5465567, -85.5461115, -85.5456662, -85.5454946, -85.5459291, -85.5463636, -85.5461919, -85.5457682, -85.5453444, -85.545162, -85.5455804, -85.5459988, -85.5458379, -85.5454088, -85.5449796, -85.5447972, -85.545221, -85.5456448, -85.5454409, -85.5450386, -85.5446362, -85.5444431, -85.5448455, -85.5452478, -85.5450332, -85.5446631, -85.5442929, -85.5441105, -85.5444914, -85.5448723, -85.5446899, -85.544309, -85.5439281, -85.543735, -85.5441213, -85.5445075, -85.5443037, -85.5439282, -85.5435526, -85.5433595, -85.543735, -85.5441105, -85.543896, -85.5435259, -85.5431557, -85.5429518, -85.5432952, -85.5436385, -85.543381, -85.5430109, -85.5426407, -85.5424368, -85.5427748, -85.5431128, -85.5428553, -85.5425173, -85.5421793, -85.5419433, -85.5422545, -85.5425656, -85.5421472, -85.541938, -85.5417287, -85.5415034, -85.5416536, -85.5418038, -85.5415249, -85.5414015, -85.5412781, -85.5410743, -85.541187, -85.5412996, -85.5410528, -85.5409348, -85.5408168, -85.5406022, -85.5406827, -85.5407631, -85.5404091, -85.5403769, -85.5403447, -85.5401409, -85.5401409, -85.5401409, -85.5399156, -85.5398941, -85.5398726, -85.5396044, -85.5396205, -85.5396366, -85.5394113, -85.5393952, -85.5393791, -85.5391002, -85.5391324, -85.5391645, -85.5389071, -85.5389017, -85.5388963, -85.5386496, -85.5386818, -85.5387139, -85.5384779, -85.5384618, -85.5384457]

slope = []
intercept = []

for i in range(0,len(lats)):
    [slat,slon] = stateplane(lats[i],lons[i])
    if i < len(lats):
        [slat2,slon2] = stateplane(lats[i+1],lons[i+1])
    else:
        [slat2,slon2] = stateplane(lats[i],lons[i])
    m = (slat-slat2)/(slon-slon2)
    b = slat-(m * slon)
    slope.append(m)
    intercept.append(b)



pwmleft = GPIO.PWM(10, 100)
pwmleft.start(14.2)
pwmright = GPIO.PWM(9, 100)
pwmright.start(14.2)

ser = serial.Serial(
    port='/dev/ttyS0',
    baudrate=115200,
    parity=serial.PARITY_NONE,
    stopbits=serial.STOPBITS_ONE,
    bytesize=serial.EIGHTBITS,
    timeout=1
)
counter = 0

time.sleep(30)

# Duty limits: 33,45,57

lstill = 14.2
rstill = 14.2
lformin = 16
lformax = 17
rformin = 17
rformax = 17.6
leftdelay = 1
rightdelay = 1

quad = 0
n = 1
g = 1
p = 1
z = 1
count = 0
wait = 0
GPIO.output(22, GPIO.LOW)
GPIO.output(27, GPIO.LOW)
GPIO.output(22, GPIO.HIGH)
GPIO.output(27, GPIO.HIGH)
time.sleep(5)
GPIO.output(22, GPIO.LOW)
GPIO.output(27, GPIO.LOW)

#Check if unicode works
def unicode(serial):
    decode = True
    parsed = [0, 0, 0, 0, 0, 0, 0, 0, 0]
    serialdecode = "0,0,0,0,0,0,0,0,0"
    try:
        serialdecode = serial.decode()
    except UnicodeError:
        decode = False
    if decode == True:
        if ',' in decode:
            parsed = serialdecode.split(",")
        else:
            parsed = [0, 0, 0, 0, 0, 0, 0, 0, 0]
    else:
        serialdecode = "0,0,0,0,0,0,0,0,0"
        parsed = serialdecode.split(",")
    return parsed

def isnumber(data, value):
    number = True
    try:
        float(data)
    except ValueError:
        number = False

    if number == True:
        num= float(value)
    else:
        num= 0

    return num

#Determine location
def location():
    valid = 1
    while valid > 0:
        pos = ser.readline()
        parsepos = unicode(pos)
        
        if parsepos[0] == '$GNVTG':
            pos = ser.readline()
            parsepos = unicode(pos)

        if parsepos[0] == '$GNGGA':
            pos = ser.readline()
            parsepos = unicode(pos)
        
        if len(parsepos) < 9:   
            deglatitude, northsouth, deglongitude, eastwest = 0,0,0,0
            
        elif len(parsepos) >= 9:
            if (parsepos[3] == '') or (parsepos[4] == '') or (parsepos[5] == '') or (parsepos[6] == ''):
                deglatitude, northsouth, deglongitude, eastwest = 0,0,0,0
                
            else:
                field3 = parsepos[3]
                deglatitude = isnumber(field3,field3)
                field5 = parsepos[5]
                deglongitude = isnumber(field5,field5)
                
                if (parsepos[4] == 'S') or (parsepos[4] == 'N'):
                    northsouth = parsepos[4]
                else:
                    northsouth = 'N'
                if (parsepos[4] == 'E') or (parsepos[6] == 'W'):
                    eastwest = parsepos[6]
                else:
                    eastwest = 'W'
                
            latitude = ((deglatitude - (deglatitude % 100)) / 100) + \
                ((deglatitude % 100) / 60)
            longitude = ((deglongitude - (deglongitude % 100)) / 100) + \
                ((deglongitude % 100) / 60)

            if northsouth == 'S':  # 4 for RMC 3 for GGA
                latitude *= -1

            if eastwest == 'W':  # 6 for RMC 5 for GGA
                longitude *= -1
            
            field8 = parsepos[8]
            course = isnumber(field8) + 90
            if parsepos[8] == '':
                course = 361
        
        meters = 0
        feet = 0

        state = stateplane.from_latlon(latitude, longitude)
        statelat = state[0]
        statelon = state[1]

        if (latitude == 0) or (longitude == 0):
            valid = 1
        else:
            valid = 0

    return [latitude, longitude, course, statelat, statelon] #add course


def distance(lat1,lon1,lat2,lon2,slope,A,B,C):
    R=6371000                               # radius of Earth in meters
    phi_1=math.radians(lat1)
    phi_2=math.radians(lat2)

    delta_phi=math.radians(lat2-lat1)
    delta_lambda=math.radians(lon2-lon1)

    a=math.sin(delta_phi/2.0)**2+\
        math.cos(phi_1)*math.cos(phi_2)*\
        math.sin(delta_lambda/2.0)**2
    c=2*math.atan2(math.sqrt(a),math.sqrt(1-a))
    
    waydist = R*c                         # output distance in meters
    pathdist = (( A * lon2)+( B * lat2) + C )/math.sqrt(( A ** 2)+1)
    #leftright = (( A * lon2)+( B * lat2) + C )
    return [waydist, pathdist]


def direction(lat1, lon1, lat2, lon2):

    if (lon2-lon1) == 0:
        traj = 90
    else:
        traj = ((math.atan((lat2-lat1)/(lon2-lon1)))*180)/math.pi

    if lat1 > lat2 and lon1 > lon2:
        traj += 180

    elif lat1 > lat2 and lon1 < lon2:
        traj += 360

    elif lat1 < lat2 and lon1 > lon2:
        traj += 180

    elif lat1 == lat2:
        traj = 0

    return traj


def turnright(timedelay):
    pwmright.ChangeDutyCycle(rformax)
    time.sleep(timedelay)
    pwmright.ChangeDutyCycle(rformin)
    time.sleep(timedelay)


def turnleft(timedelay):
    pwmleft.ChangeDutyCycle(lformax)
    time.sleep(timedelay)
    pwmleft.ChangeDutyCycle(lformin)
    time.sleep(timedelay)


def bigright():
    pwmright.ChangeDutyCycle(rformax)
    pwmleft.ChangeDutyCycle(lstill)
    time.sleep(2)
    pwmright.ChangeDutyCycle(rformin)
    pwmleft.ChangeDutyCycle(lformin)
    time.sleep(2)


def bigleft():
    pwmleft.ChangeDutyCycle(lformax)
    pwmright.ChangeDutyCycle(rstill)
    time.sleep(2)
    pwmleft.ChangeDutyCycle(lformin)
    pwmright.ChangeDutyCycle(rformin)
    time.sleep(2)


while n > 0:
    RMC = location()
    
    if RMC[0] == 0:
        n = 1

    else:
        n = 0
    wait += 1

    if wait > 120:
        n = 0

    time.sleep(1)


# FIRST POINT (WAYPOINT)
RMC = location()
waylat1 = RMC[3]
waylon1 = RMC[4]

#waylat1 = 36.1992700600613
#waylon1 = -85.51498414971903
GPIO.output(27, GPIO.HIGH)
pwmright.ChangeDutyCycle(rformax)
pwmleft.ChangeDutyCycle(lformax)
#time.sleep(20)
'''
while p > 0:
    RMC = location()
    waylat2 = RMC[0]
    waylon2 = RMC[1]
    dist = math.sqrt(((waylat1-waylat2)**2)+((waylon1-waylon2)**2))
    if dist > 0.00003:
        p = 0
    else:
        p = 1
    time.sleep(1)
'''
RMC = location()
waylat2 = RMC[0]
waylon2 = RMC[1]
count = 0

if (waylon2-waylon1)==0:
    slope = 1000
else:
    slope = (waylat2-waylat1)/(waylon2-waylon1)
d = waylat1-(slope * waylon1)

pslope = (1 / slope )*-1
e = waylat1-( pslope * waylon1)

# VARIABLES FOR PATH DISTANCE
a = -slope 
b = 1
c = -d

r = -pslope 
s = 1
t = -e


# PATH DIRECTION
waydir = direction(waylat2, waylon2, waylat1, waylon1)

if waydir < 10:
    dirmin = 360-(10-waydir)
    dirmax = waydir + 10

elif waydir >= 350:
    dirmin = waydir - 10
    dirmax = 10-(360-waydir)

else:
    dirmin = waydir - 10
    dirmax = waydir + 10

if waydir == 10:
    dirmin = 0
    dirmax = 20

if waydir == 350:
    dirmin = 340
    dirmax = 0

if waydir > 0:
    quad = 1

if waydir > 90:
    quad = 2

if waydir > 180:
    quad = 3

if waydir > 270:
    quad = 4






GPIO.output(22, GPIO.HIGH)
time.sleep(2)
# START MOVING
pwmright.ChangeDutyCycle(rformin)
pwmleft.ChangeDutyCycle(lformin)
time.sleep(2)

# START RECORDING
RMC = location()
lat1 = RMC[0]
lon1 = RMC[1]
time.sleep(2)
#angle = RMC[2]
waydist1 = math.sqrt(((waylat1-lat1)**2)+((waylon1-lon1)**2))
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

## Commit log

2022-04-22 Rename Software/readme.md to Software/Raspberry Pi/readme.md
2022-04-22 Rename Software/autonomous_hsv.py to Software/Raspberry Pi/autonomous_hsv.py
